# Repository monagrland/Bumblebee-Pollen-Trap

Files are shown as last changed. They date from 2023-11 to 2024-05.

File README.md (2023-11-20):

# Pollenstripper
 
This repository contains .scad and STL files as well as json presets for the bumblebee pollenstripper as described in Krüger et al

## Printing the Files

If you just want to print the files used in Krüger et al, you can go to the "STL_Files" directory and download all STL files that you want to print. Almost all files can be easily printed in PLA or PETG. If you want to use the pollen for DNA sequencing, we would recommend to use thermostable materials like ASA or ABS, to be able to clean the parts with boiling water. Almost all files can be printed without supports, with the exception of the funnel. The corpus minorly profits from supports but they are not a necessity.

# DIY Pollenstripper
## Getting Started
Do you have ideas to improve the Pollenstripper? Feel free to modify the design however you want. A lot of modifications can be done without any knowledge in 3D-Design. All you need are the files in this repository and the open source software [OpenSCAD](https://openscad.org/). It can be freely downloaded from the website. 

After installing OpenSCAD you can download this repository by clicking on "Code" and selecting "Download ZIP". After finishing the download you can unpack the directory to you prefered path.
Now you can chose which parts you want to modify. 

If you want to modify the corpus, the darkener or the funnel, you can open the corpus_designer.scad file with OpenSCAD. If you want to modify the filter inserts, you can open the filter_designer.scad file with OpenSCAD.
After opening the file you should see by default four different windows. On the Left the **Editor** shows you the code used to create the designs. On the bottom you can see the **Console**, which offers information about the rendering and if there were occuring errors. In the middle you can see the current preview of your 3D-Object. On the fourth panel on the right you can find the **Customizer**. If the Customizer is not open, you can open it by clicking on the **Window** menu and unselecting the **Hide customizer** option.
You can update the preview by pressing F5 and you can render the model with F6.

For further information about OpenSCAD, take a look at the [docs](https://openscad.org/documentation.html).  

## DIY Corpus, Darkener, Funnel & Brush-Corpus
If you want to modify the corpus, the darkener, the funnel or the brush-corpus you have two different options: either you use the customizer and play around with the options available without the need of any knowledge regarding 3D-design or programming or you can modify the code itself to create something completely custom. 
If you want to use the customizer, the variables are seperated into different tabs.

### Presets
If you don't want to create your designs from scratch, you can also use one of the available presets. You can find the presets at the top of the customizer. The preset *corpus* contains the settings for the corpus used in Krüger et al, while the preset *corpus with grid* has the same settings but with a grid at the bottom of the corpus. The *darkener* preset contains the settings for the darkener used in Krüger et al.

### Parameters
In the `Parameters` tab you can select which part you want to create or modify. 

### Acrylic Cube
In the `Acrylic Cube` tab you can select the dimensions of the acrylic cube that you are going to use. This is important for all designs since they are automaticallly modified to fit differently sized acrylic cubes.

### Darkener
The `Darkener` tab contains variables that are only relevant if you want to modify the darkener.

### Insert
In the `Insert` tab you have to enter the dimensions of the filter inserts that are created with the filter_designer.scad file. This is important for the corpus and brush-corpus designs so that the filter inserts fit into the slots.
You can also modify the positioning of the slot and the space between the filter insert and the corpus. 

### Corpus Basics
The `Corpus Basics` tab containts the variables that are used to create the corpus design. The first part of the corpus depends on the size of the acrylic cube and has to be modified in the corresponding tab. The second part of the corpus is made out of "tubes", which are basically small chambers which each contain a single slot for a filter insert. You can modify the dimensions of these tubes and the amount of tubes that are put behind each other to modify the amount of "chambers" the bumblebee has to cross.

### Grid Pattern
In earlier iterations, the corpus had a grid at the bottom where the pollen was supposed to fall through. In our testing this did not work as expected, which is why the grid was removed to decrease the amount of light that falls into the chambers to focus the bumblebees more into the direction of the exit. If you want you can create the grid in this tab and modify the dimensions and the amount of the squared holes in the corpus.

### Brush
We tested a version of the pollenstripper where brushes were mounted at an angle allowing the bumblebee to press itself through the middle between the brushes. This version did not succeed in any case, but if you want to modify it you can change the parameters at the `Brush` tab.

### Funnel
Earlier iterations had a grid where the pollen was supposed to fall through (see grid tab). Aterwards the pollen was supposed to fall into a funnel which could be slid onto the corpus with a thread for 2ml microcentrifuge tubes at the bottom. If you want to create or modify this funnel, you can find the needed variables at the `Funnel` tab.

### Misc
The `Misc` tab only contains the $fn variable which is used to define the number of fragments used to draw an arc. A higher value creates smoother arcs but also significantly increases the rendering time. If you just want to play around with the values i would recommend a lower $fn, for example 25, and to later increase it after you finished your model and create the rendering for the export of the file. My recommendation herefore would be a value of 100.

## DIY Filter Inserts
If you want to create or modify the filter inserts, you can either use the customizer and play around with the options available without the need of any knowledge regarding 3D-Design or programming or you can modify the code itself to create something completely custom
If you want to use the customizer, the variables here are also seperated into different tabs.

### Presets
If you don't want to create your designs from scratch, you can also use one of the available presets. You can find the presets at the top of the customizer. The preset *Preset a* contains the settings for the filter insert *a* as described in Krüger et al, while *Preset b* and *Preset c* are used for the other two described filter inserts. To recreate all filter inserts from the publication you can select the presets and just edit the diameter of the hole inside the `Base Plate` tab. 

### Base Plate
The `Base Plate` tab allows changes to the dimensions of the base plate, the bars on the base plate as well as the text on top of the base plate.

### Hole Structure
In the `Hole Structure` tab you select which one of the five possible designs you want to use.
You can choose if you want no structure ("None"), slides (used in version *a* in Krüger et al.), two different triangle structures ("triangle" and "triangle2", used in version *b* and *c*, respectively) (used in version c) or concentric (untested idea using concentric circles). 

### Hole Structure == Slides
If you chose the "slides" hole structure in the `Hole Structure` tab, you can edit the remainding variables in the `Hole Structure == Slides` tab. Here you can change the dimensions of the rings as well as the dimensions, offset and number of slides.

### Hole Structure == Triangle
If you chose the "triangle" hole structure in the `Hole Structure` tab, you can edit the remainding variables in the `Hole Structure == Triangle` tab. Here you can change the dimensions of the rings as well as the dimensions and number of triangles.

### Hole Structure == Triangle2
If you chose the "triangle2" hole structure in the `Hole Structure` tab, you can edit the remainding variables in the `Hole Structure == Triangle2` tab. Here you can change the dimensions of the rings as well as the dimensions and number of triangles.

### Hole Structure == Concentric
If you chose the "concentric" hole structure in the `Hole Structure` tab, you can edit the remainding variables in the `Hole Structure == Concentric` tab. Here you can change the dimensions and positioning of the concentric rings.

### Misc
The `Misc` tab only contains the $fn variable which is used to define the number of fragments used to draw an arc. A higher value creates smoother arcs but also significantly increases the rendering time. If you just want to play around with the values I would recommend a lower $fn, for example 25, and to later increase it after you finished your model and create the rendering for the export of the file. My recommendation therefore would be a value of 100.

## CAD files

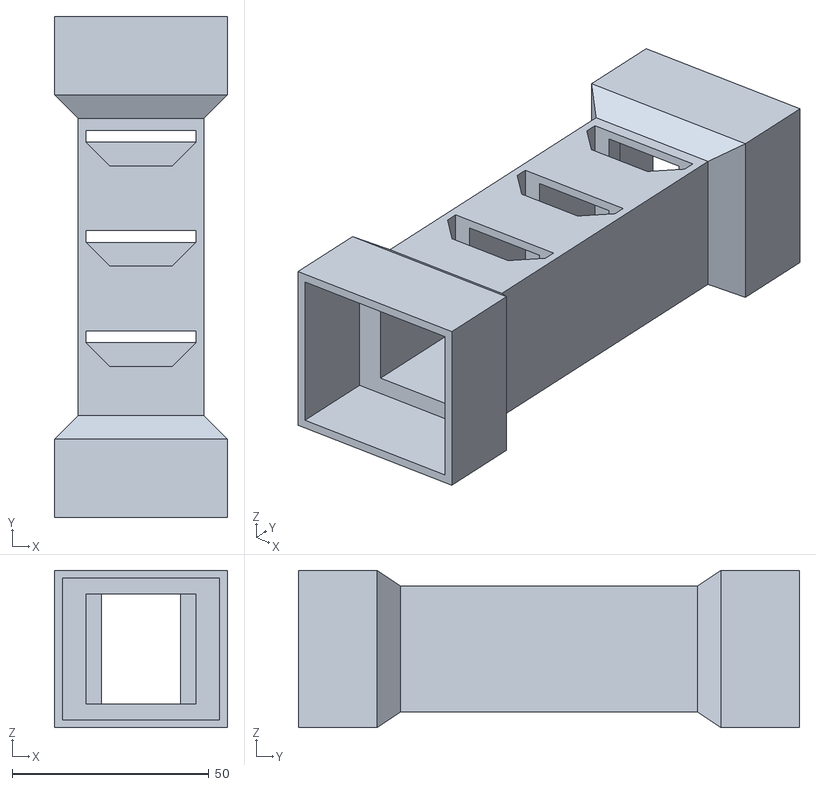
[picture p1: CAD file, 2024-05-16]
STL_Files/Corpus_Double_Cube.stl
44.0 x 127.5 x 40.0

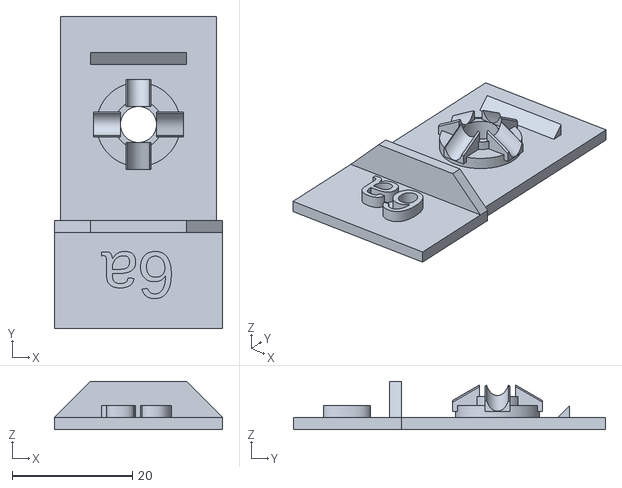
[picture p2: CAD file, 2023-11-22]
STL_Files/a_6_0.stl
28.0 x 52.0 x 8.00

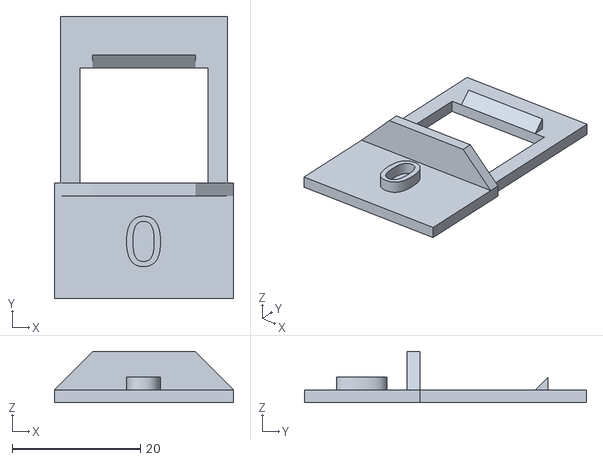
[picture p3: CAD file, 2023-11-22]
STL_Files/Filter_Brush.stl
28.0 x 44.0 x 8.00

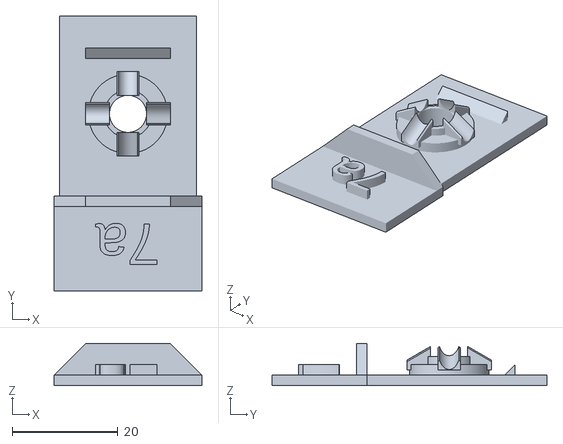
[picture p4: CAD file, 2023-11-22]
STL_Files/a_7_0.stl
28.0 x 52.0 x 8.00

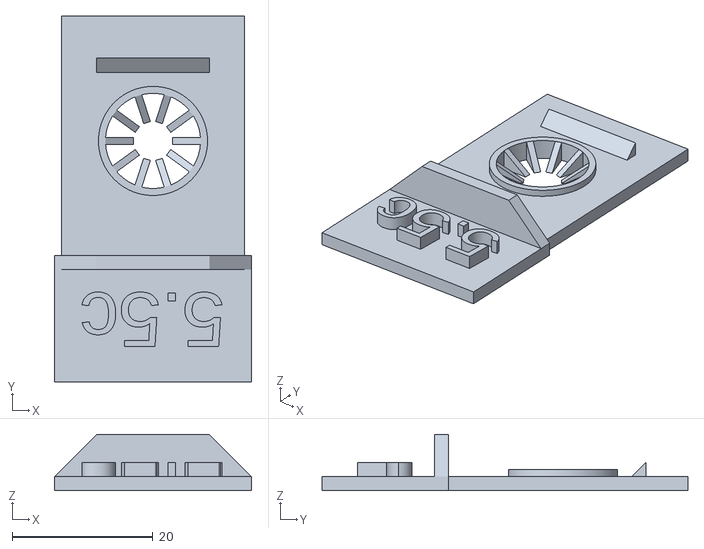
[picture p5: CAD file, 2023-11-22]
STL_Files/c_5_5.stl
28.0 x 52.0 x 8.00

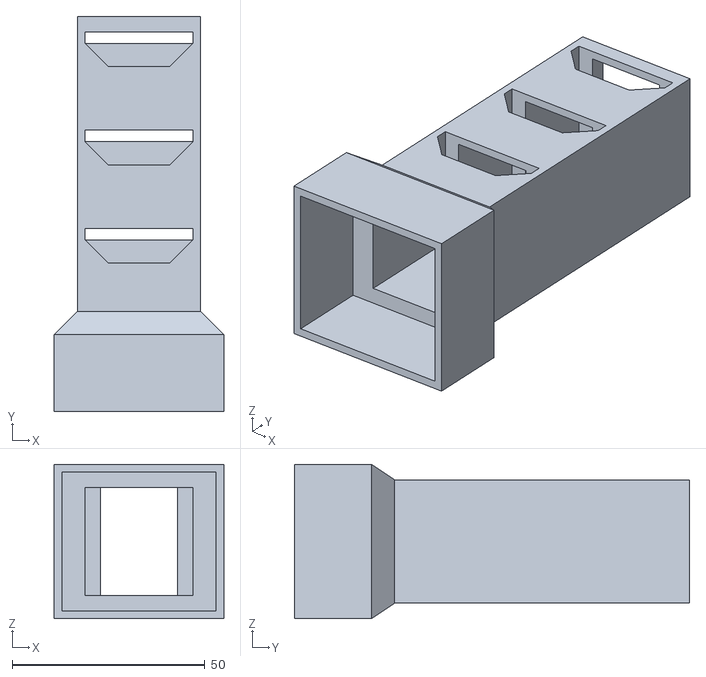
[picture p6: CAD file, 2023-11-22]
STL_Files/Corpus_sans_holes.stl
44.0 x 102.5 x 40.0

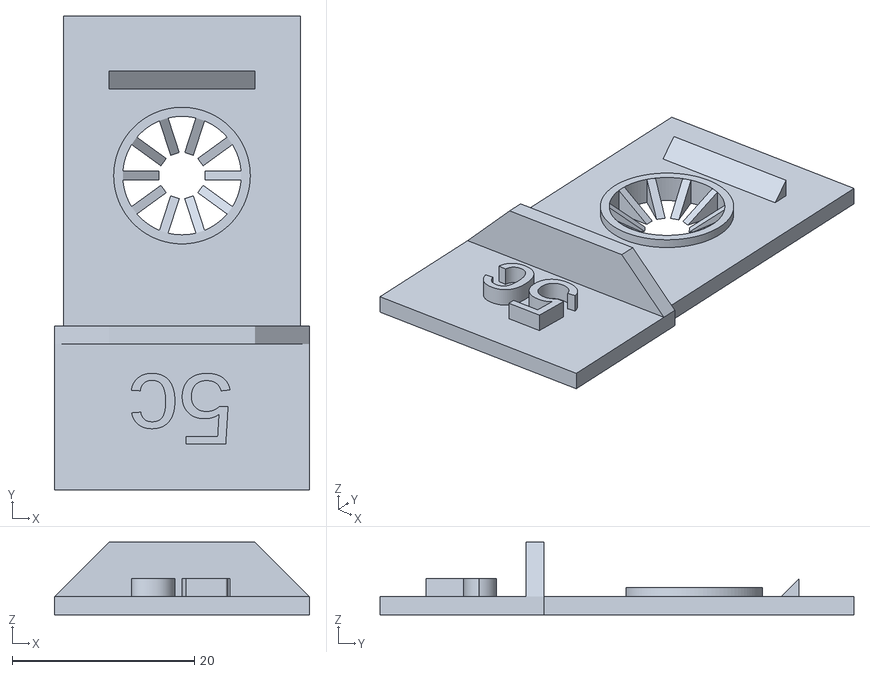
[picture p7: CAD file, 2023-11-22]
STL_Files/c_5_0.stl
28.0 x 52.0 x 8.00

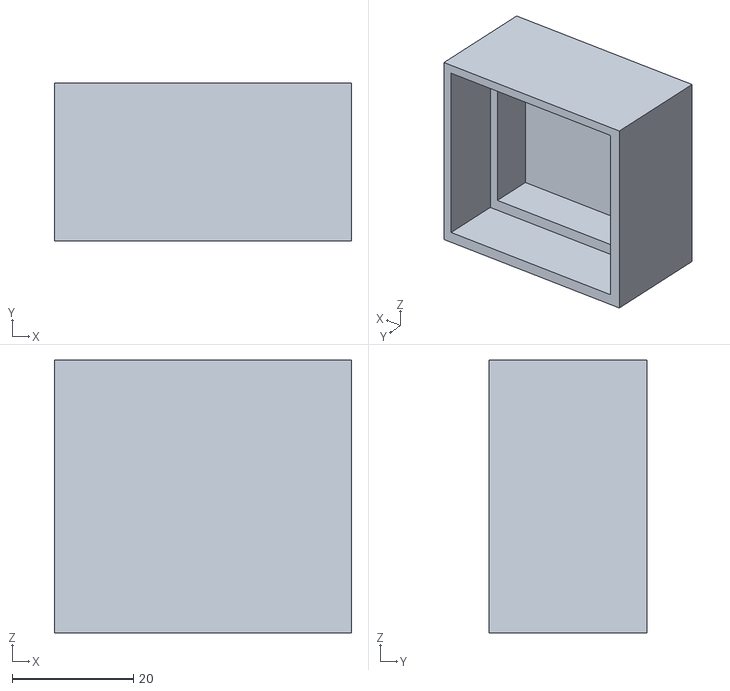
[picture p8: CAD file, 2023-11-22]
STL_Files/Darkener.stl
49.0 x 26.0 x 45.0

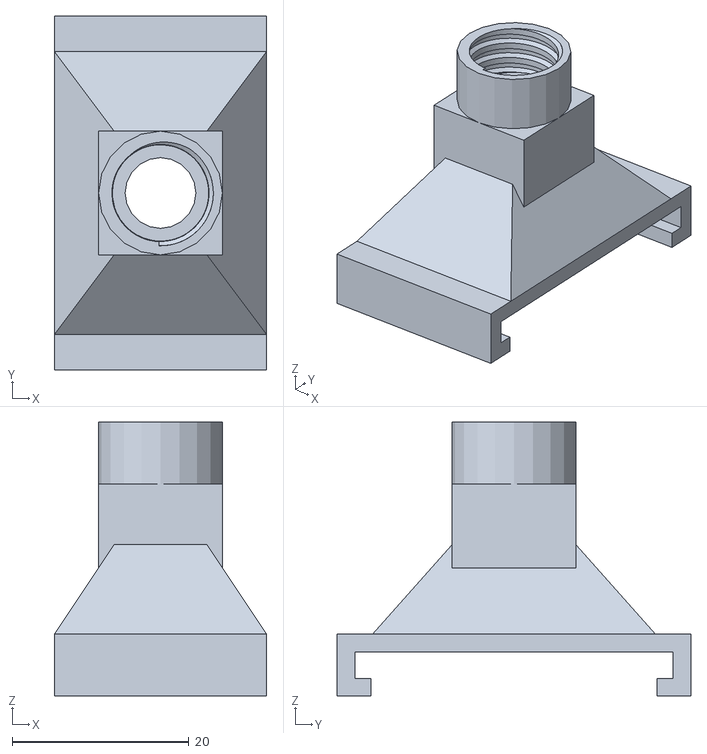
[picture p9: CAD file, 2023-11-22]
STL_Files/Funnel_Brush.stl
24.0 x 40.0 x 31.0

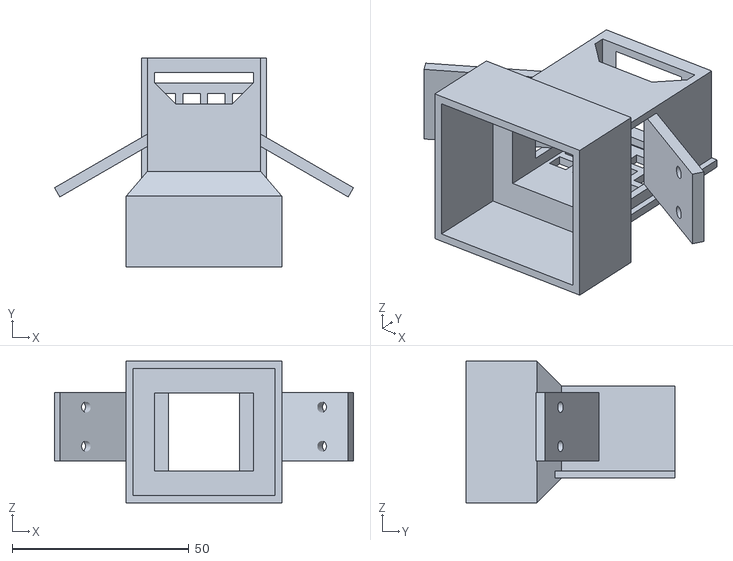
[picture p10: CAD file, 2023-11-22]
STL_Files/Corpus_Brush.stl
84.5 x 59.0 x 40.0

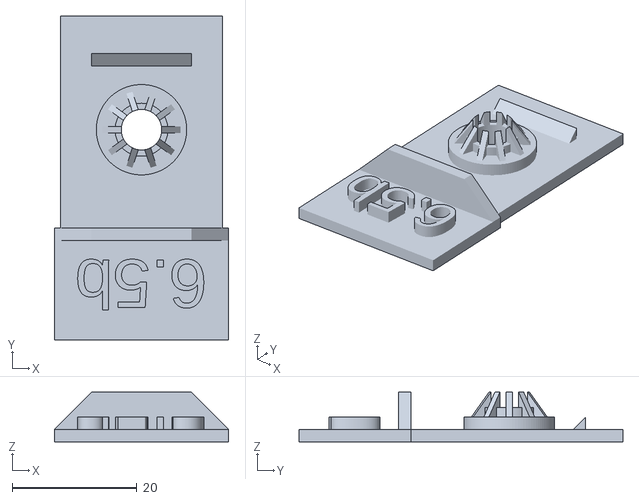
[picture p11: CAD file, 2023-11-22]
STL_Files/b_6_5.stl
28.0 x 52.0 x 8.00

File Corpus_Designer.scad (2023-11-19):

 //Variables
// Select which part you want to create: corpus is the main part of the pollenstripper, corpus_brush is a version of the pollenstripper with angled mounts for brushes, the darkener is a part that sits on top of the plexiglas cube to keep light from getting in and the funnel was meant to collect the pollen after it fell off and through the grid (deprecated)
cube_design = "corpus"; // [corpus, corpus_brush, darkener, funnel]

/* [Acrylic Cube] */
plexi_cube_width = 39; //39 for cube1, 32 for cube2
plexi_cube_length = 35; //35 for cube1, 30 for cube2
plexi_cube_depth_overall = 30;
plexi_cube_depth = 20; //this is for the main corpus
plexi_cube_thickness = 2;
plexi_cube_buffer = 0.5; //1mm room in every direction

/* [Darkener] */
// The length that the darkener overlaps with the corpus
darkener_overhang = 10;

/* [Insert] */
//needs to be the same as in the insert creator
insert_bar_height = 6;
//needs to be the same as in the insert creator
insert_bar_length = 16;
//needs to be the same as "base plate length upper" in the insert creator
insert_base_length = 28;
//needs to be the same as "base plate thickness" in the insert creator
insert_thickness = 2;
// buffer space between corpus and insert
insert_buffer = 1;
// distance of the insert from the end of the tube. CAREFUL: changing this can break the design, default=4
insert_distance_from_tube_end = 4;

/* [Corpus Basics] */
//thickness of the tubes (lower parts of the corpus containing the inserts)
tube_thickness = 2;
//width of the tubes
tube_width = 28;
//length of the tubes
tube_length = 28;
//depth of the tubes, 25.5 for normal corpus design, 32 for brush
tube_depth = 25.5; // was 38.5, for normal design 25.5, increase for brush to 32
//number of tubes
tube_count = 3;

// width of the bar that locks the inserts so that they can't move to the back, CAREFUL: changing this will break the design, default = 4
security_bar_width = 4;
slide_bar_length = tube_depth+2;
// width of the bar the funnel slides on
slide_bar_width = 1.6; //decreased from 2 to 1,6 for buffer
//height of the bar the funnel slides on
slide_bar_height = 2;

/* [Grid Pattern] */
// grid pattern, meant to let the stripped pollen fall through into the funnel
grid_pattern = "None"; //[None, squares, squares2]
//width of the squares
square_width = 5;
//length of the squares
square_length = 4;
//distance between the squares
square_distance = 2;
//number oif squares per row
number_squares_per_row = 4;
//number of squares per column, suggestion for normal corpus 2, for brush 3
number_squares_per_column = 3;

/* [Brush] */
// length of the top part of the brush
brush_head_length = 16;
// length of the bottom part of the brush
brush_bottom_length = 24;
// width of the brush
brush_width = 19.25;
// thickness of the brush
brush_thickness = 5.5;
// distance of the screw holes from the top of the brush
distance_hole_from_top = 1.6;
// distance of the screw holes from the side of the brush
distance_hole_from_side = 2.6;
// diameter of the screw holes
diameter = 3;

/* [Funnel] */
// width of the bars that slide on the corpus
funnel_slide_width = 4;
// height of the bars that slide on the corpus
funnel_slide_height = 7;
// height of the hollow part of the bars that slide on the corpus
funnel_slide_hollow_height = 3;
// buffer between the corpus bar and the funnel slide bar
funnel_slide_buffer_width = 0.2;
// length of the pyramid
funnel_pyramid_length = 32;
// height of the tip of the pyramid part
funnel_pyramid_tip_height = 18;
// width of the cube at the top of the funnel
funnel_tip_cube_width = 14;
// length of the cube at the top of the funnel
funnel_tip_cube_length = 14;
// height of the cube at the top of the funnel
funnel_tip_cube_height = 11;
// height of the cylinder that hollows out the top of the funnel
funnel_hollow_cylinder_height = 20;
// diameter of the cylinder that hollows out the top of the funnel
funnel_hollow_cylinder_diameter = 7;



/* [Misc] */
// Number of Faces: higher number is good for smoother curved areas, lower number significantly decreases rendering time, recommending 25 for playing around and 100 for exporting
$fn = 50;

//angle
tube_distance_left = (plexi_cube_width/2+plexi_cube_buffer+plexi_cube_thickness-tube_width/2-tube_thickness);
tube_distance_bottom = (plexi_cube_length/2+plexi_cube_buffer+plexi_cube_thickness-tube_length/2-tube_thickness);
angle_depth = max(tube_distance_left, tube_distance_bottom);
outer_cube_width = plexi_cube_width + 2*plexi_cube_thickness + 2*plexi_cube_buffer;
outer_cube_length = plexi_cube_length + 2*plexi_cube_thickness + 2*plexi_cube_buffer;

//module to create triangles
module triangle(width,length,height){
    difference(){
        cube([width,length,height]);
        rotate([0,0,45]) cube([width*2.5,length*2.5,height*5]);
    }
}

//module to show points of a polyhedron
module showPoints(v) {
    for (i = [0: len(v)-1]) {
        translate(v[i]) color("red") 
        text(str(i), font = "Courier New", size=1.5);
         
    }
}

//module to create a square grid pattern
module square_grid(){
    grid_width = square_width*number_squares_per_row + square_distance*(number_squares_per_row-1);
    grid_length = square_length*number_squares_per_column + square_distance*(number_squares_per_column-1);
translate([tube_width/2+tube_thickness-grid_width/2,tube_depth+angle_depth-(insert_distance_from_tube_end+insert_thickness+insert_buffer+insert_bar_height)+3,0])
translate([grid_width,0,0])
rotate([0,0,180])
for (j=[0:number_squares_per_column-1]){
for (i=[0:number_squares_per_row-1]){
    translate([i*(square_distance+square_width),j*(square_distance+square_length),0])cube([square_width,square_length,tube_thickness]);
    }
}
}

module square_grid2(){
    grid_width = square_width*number_squares_per_row + square_distance*(number_squares_per_row-1);
    grid_length = square_length*number_squares_per_column + square_distance*(number_squares_per_column-1);
translate([tube_width/2+tube_thickness-grid_width/2,tube_depth+angle_depth-(insert_distance_from_tube_end+insert_thickness+insert_buffer+insert_bar_height),0])
translate([grid_width-square_length/2,0,0])
rotate([0,0,180])
for (j=[0:number_squares_per_column-1]){
for (i=[0:number_squares_per_row-1]){
    translate([i*(square_distance+square_width),j*(square_distance+square_length),0])rotate([0,0,45])cube([square_width,square_length,tube_thickness]);
    }
}
}

//module to create a brush as a standin
module brush (){
difference(){
union(){
color("green")cube([brush_width, brush_thickness, brush_head_length]);
color("brown")translate([0,0,brush_head_length])cube([brush_width, brush_thickness, brush_bottom_length]);
}

union(){
translate([diameter/2+distance_hole_from_side,0,diameter/2 + distance_hole_from_top])rotate([270,0,0])cylinder(h=brush_thickness, d=diameter);
translate([brush_width-diameter/2-distance_hole_from_side,0,diameter/2 + distance_hole_from_top])rotate([270,0,0])cylinder(h=brush_thickness, d=diameter);
}
}
}

//module to create a mount for the brush
module brush_mount (){
difference(){
union(){
color("green")cube([brush_width, brush_thickness, brush_head_length]);
color("brown")translate([0,0,brush_head_length])cube([brush_width, brush_thickness, brush_bottom_length]);
}

union(){
translate([diameter/2+distance_hole_from_side,0,diameter/2 + distance_hole_from_top])rotate([270,0,0])cylinder(h=brush_thickness, d=diameter);
translate([brush_width-diameter/2-distance_hole_from_side,0,diameter/2 + distance_hole_from_top])rotate([270,0,0])cylinder(h=brush_thickness, d=diameter);
}
}
}


if (cube_design == "corpus"){
union(){

//plexi_cube part of the tube
difference(){
    cube([plexi_cube_width + 2*plexi_cube_thickness + 2*plexi_cube_buffer, plexi_cube_depth, plexi_cube_length+2*plexi_cube_thickness + 2*plexi_cube_buffer]);
    translate([plexi_cube_thickness,0,plexi_cube_thickness])cube([plexi_cube_width + 2*plexi_cube_buffer, plexi_cube_depth, plexi_cube_length + 2*plexi_cube_buffer]);
}

//angle
angle_points = [
    [0,0,0], //0
    [outer_cube_width,0,0],//1
    [outer_cube_width,0,outer_cube_length],//2
    [0,0,outer_cube_length],//3
    [tube_distance_left,0,tube_distance_bottom],//4
    [outer_cube_width-tube_distance_left,0,tube_distance_bottom],//5
    [outer_cube_width-tube_distance_left,0,outer_cube_length-tube_distance_bottom],//6
    [tube_distance_left,0,outer_cube_length-tube_distance_bottom],//7
    [tube_distance_left,angle_depth,tube_distance_bottom],//8
    [outer_cube_width-tube_distance_left,angle_depth,tube_distance_bottom],//9
    [outer_cube_width-tube_distance_left,angle_depth,outer_cube_length-tube_distance_bottom],//10
    [tube_distance_left,angle_depth,outer_cube_length-tube_distance_bottom],//11
    
];

*showPoints(angle_points);
angle_faces = [
    [1,0,4,5],
    [0,1,9,8],
    [5,4,8,9],
    [2,1,5,6],
    [1,2,10,9],
    [6,5,9,10],
    [3,2,6,7],
    [2,3,11,10],
    [7,6,10,11],
    [0,3,7,4],
    [3,0,8,11],
    [4,7,11,8],
];
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

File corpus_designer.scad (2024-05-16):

 //Variables
// Select which part you want to create: corpus is the main part of the pollenstripper, corpus_brush is a version of the pollenstripper with angled mounts for brushes, the darkener is a part that sits on top of the plexiglas cube to keep light from getting in and the funnel was meant to collect the pollen after it fell off and through the grid (deprecated)
cube_design = "corpus"; // [corpus, corpus_dual_cube, corpus_brush, darkener, funnel]

/* [Acrylic Cube] */
plexi_cube_width = 39; //39 for cube1, 32 for cube2
plexi_cube_length = 35; //35 for cube1, 30 for cube2
plexi_cube_depth_overall = 30;
plexi_cube_depth = 20; //this is for the main corpus
plexi_cube_thickness = 2;
plexi_cube_buffer = 0.5; //1mm room in every direction

/* [Acrylic Cube 2: Only necessary for dual cube corpus] */
plexi_cube_width2 = 39; //39 for cube1, 32 for cube2
plexi_cube_length2 = 35; //35 for cube1, 30 for cube2
plexi_cube_depth_overall2 = 30;
plexi_cube_depth2 = 20; //this is for the main corpus
plexi_cube_thickness2 = 2;
plexi_cube_buffer2 = 0.5; //1mm room in every direction

/* [Darkener] */
// The length that the darkener overlaps with the corpus
darkener_overhang = 10;

/* [Insert] */
//needs to be the same as in the insert creator
insert_bar_height = 6;
//needs to be the same as in the insert creator
insert_bar_length = 16;
//needs to be the same as "base plate length upper" in the insert creator
insert_base_length = 28;
//needs to be the same as "base plate thickness" in the insert creator
insert_thickness = 2;
// buffer space between corpus and insert
insert_buffer = 1;
// distance of the insert from the end of the tube. CAREFUL: changing this can break the design, default=4
insert_distance_from_tube_end = 4;

/* [Corpus Basics] */
//thickness of the tubes (lower parts of the corpus containing the inserts)
tube_thickness = 2;
//width of the tubes
tube_width = 28;
//length of the tubes
tube_length = 28;
//depth of the tubes, 25.5 for normal corpus design, 32 for brush
tube_depth = 25.5; // was 38.5, for normal design 25.5, increase for brush to 32
//number of tubes
tube_count = 3;

// width of the bar that locks the inserts so that they can't move to the back, CAREFUL: changing this will break the design, default = 4
security_bar_width = 4;
slide_bar_length = tube_depth+2;
// width of the bar the funnel slides on
slide_bar_width = 1.6; //decreased from 2 to 1,6 for buffer
//height of the bar the funnel slides on
slide_bar_height = 2;

/* [Grid Pattern] */
// grid pattern, meant to let the stripped pollen fall through into the funnel
grid_pattern = "None"; //[None, squares, squares2]
//width of the squares
square_width = 5;
//length of the squares
square_length = 4;
//distance between the squares
square_distance = 2;
//number oif squares per row
number_squares_per_row = 4;
//number of squares per column, suggestion for normal corpus 2, for brush 3
number_squares_per_column = 3;

/* [Brush] */
// length of the top part of the brush
brush_head_length = 16;
// length of the bottom part of the brush
brush_bottom_length = 24;
// width of the brush
brush_width = 19.25;
// thickness of the brush
brush_thickness = 5.5;
// distance of the screw holes from the top of the brush
distance_hole_from_top = 1.6;
// distance of the screw holes from the side of the brush
distance_hole_from_side = 2.6;
// diameter of the screw holes
diameter = 3;

/* [Funnel] */
// width of the bars that slide on the corpus
funnel_slide_width = 4;
// height of the bars that slide on the corpus
funnel_slide_height = 7;
// height of the hollow part of the bars that slide on the corpus
funnel_slide_hollow_height = 3;
// buffer between the corpus bar and the funnel slide bar
funnel_slide_buffer_width = 0.2;
// length of the pyramid
funnel_pyramid_length = 32;
// height of the tip of the pyramid part
funnel_pyramid_tip_height = 18;
// width of the cube at the top of the funnel
funnel_tip_cube_width = 14;
// length of the cube at the top of the funnel
funnel_tip_cube_length = 14;
// height of the cube at the top of the funnel
funnel_tip_cube_height = 11;
// height of the cylinder that hollows out the top of the funnel
funnel_hollow_cylinder_height = 20;
// diameter of the cylinder that hollows out the top of the funnel
funnel_hollow_cylinder_diameter = 7;



/* [Misc] */
// Number of Faces: higher number is good for smoother curved areas, lower number significantly decreases rendering time, recommending 25 for playing around and 100 for exporting
$fn = 50;

//angle
tube_distance_left = (plexi_cube_width/2+plexi_cube_buffer+plexi_cube_thickness-tube_width/2-tube_thickness);
tube_distance_bottom = (plexi_cube_length/2+plexi_cube_buffer+plexi_cube_thickness-tube_length/2-tube_thickness);
angle_depth = max(tube_distance_left, tube_distance_bottom);
outer_cube_width = plexi_cube_width + 2*plexi_cube_thickness + 2*plexi_cube_buffer;
outer_cube_length = plexi_cube_length + 2*plexi_cube_thickness + 2*plexi_cube_buffer;

//angle2
tube_distance_left2 = (plexi_cube_width2/2+plexi_cube_buffer2+plexi_cube_thickness2-tube_width/2-tube_thickness);
tube_distance_bottom2 = (plexi_cube_length2/2+plexi_cube_buffer2+plexi_cube_thickness2-tube_length/2-tube_thickness);
angle_depth2 = max(tube_distance_left2, tube_distance_bottom2);
outer_cube_width2 = plexi_cube_width2 + 2*plexi_cube_thickness2 + 2*plexi_cube_buffer2;
outer_cube_length2 = plexi_cube_length2 + 2*plexi_cube_thickness2 + 2*plexi_cube_buffer2;

//module to create triangles
module triangle(width,length,height){
    difference(){
        cube([width,length,height]);
        rotate([0,0,45]) cube([width*2.5,length*2.5,height*5]);
    }
}

//module to show points of a polyhedron
module showPoints(v) {
    for (i = [0: len(v)-1]) {
        translate(v[i]) color("red") 
        text(str(i), font = "Courier New", size=1.5);
         
    }
}

//module to create a square grid pattern
module square_grid(){
    grid_width = square_width*number_squares_per_row + square_distance*(number_squares_per_row-1);
    grid_length = square_length*number_squares_per_column + square_distance*(number_squares_per_column-1);
translate([tube_width/2+tube_thickness-grid_width/2,tube_depth+angle_depth-(insert_distance_from_tube_end+insert_thickness+insert_buffer+insert_bar_height)+3,0])
translate([grid_width,0,0])
rotate([0,0,180])
for (j=[0:number_squares_per_column-1]){
for (i=[0:number_squares_per_row-1]){
    translate([i*(square_distance+square_width),j*(square_distance+square_length),0])cube([square_width,square_length,tube_thickness]);
    }
}
}

module square_grid2(){
    grid_width = square_width*number_squares_per_row + square_distance*(number_squares_per_row-1);
    grid_length = square_length*number_squares_per_column + square_distance*(number_squares_per_column-1);
translate([tube_width/2+tube_thickness-grid_width/2,tube_depth+angle_depth-(insert_distance_from_tube_end+insert_thickness+insert_buffer+insert_bar_height),0])
translate([grid_width-square_length/2,0,0])
rotate([0,0,180])
for (j=[0:number_squares_per_column-1]){
for (i=[0:number_squares_per_row-1]){
    translate([i*(square_distance+square_width),j*(square_distance+square_length),0])rotate([0,0,45])cube([square_width,square_length,tube_thickness]);
    }
}
}

//module to create a brush as a standin
module brush (){
difference(){
union(){
color("green")cube([brush_width, brush_thickness, brush_head_length]);
color("brown")translate([0,0,brush_head_length])cube([brush_width, brush_thickness, brush_bottom_length]);
}

union(){
translate([diameter/2+distance_hole_from_side,0,diameter/2 + distance_hole_from_top])rotate([270,0,0])cylinder(h=brush_thickness, d=diameter);
translate([brush_width-diameter/2-distance_hole_from_side,0,diameter/2 + distance_hole_from_top])rotate([270,0,0])cylinder(h=brush_thickness, d=diameter);
}
}
}

//module to create a mount for the brush
module brush_mount (){
difference(){
union(){
color("green")cube([brush_width, brush_thickness, brush_head_length]);
color("brown")translate([0,0,brush_head_length])cube([brush_width, brush_thickness, brush_bottom_length]);
}

union(){
translate([diameter/2+distance_hole_from_side,0,diameter/2 + distance_hole_from_top])rotate([270,0,0])cylinder(h=brush_thickness, d=diameter);
translate([brush_width-diameter/2-distance_hole_from_side,0,diameter/2 + distance_hole_from_top])rotate([270,0,0])cylinder(h=brush_thickness, d=diameter);
}
}
}


if (cube_design == "corpus"){
union(){

//plexi_cube part of the tube
difference(){
    cube([plexi_cube_width + 2*plexi_cube_thickness + 2*plexi_cube_buffer, plexi_cube_depth, plexi_cube_length+2*plexi_cube_thickness + 2*plexi_cube_buffer]);
    translate([plexi_cube_thickness,0,plexi_cube_thickness])cube([plexi_cube_width + 2*plexi_cube_buffer, plexi_cube_depth, plexi_cube_length + 2*plexi_cube_buffer]);
}
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

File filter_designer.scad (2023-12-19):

//Variables
/* [Base Plate] */
//length of the lower part of the base plate
base_plate_length_lower = 26;
//length of the upper part of the base plate
base_plate_length_upper = 28;
//width of the lower part of the base plate
base_plate_width_lower = 34;
//length of the upper part of the base plate
base_plate_width_upper = 18;
//thickness of the baseplate
base_plate_thickness = 2;
// type of bar, newer versions only use "angled"
bar_type = "angled"; // [angled, bar]
// length of the bar
bar_length = 16;
// width of the bar
bar_width = 2;
// height of the bar
bar_height = 6;

//diameter of the hole, also input for the text at the top
diameter_hole = 5.5;
// thickness of the text at the top
diameter_text_thickness = 2;
// size of the text at the top
diameter_text_size = 8;

// additional text at the top
identifier = "a";

// width of the lower bar
lower_bar_width = 2;
// height of the lower bar
lower_bar_height = 2;
// distance from the bottom of the base plate to the lower bar
lower_bar_distance_from_bottom = 6;

/* [Hole Structure] */
// structure of the design around the hole
hole_structure = "triangle2"; //  [None, slides, triangle, triangle2, concentric, brush]

/* [Hole Structure == Slides] */
// width of the outer ring
outer_ring_width_slides = 4.0;
// height of the outer ring
outer_ring_height_slides = 2.0;
// width of the inner ring
inner_ring_width_slides = 1.0;
// height of the outer ring
inner_ring_height_slides = 1.5;
// number of slides, will be automatically oriented around the center of the hole
number_slides = 4;

// multiplier for the width of the slides
slide_width_factor = 0.7;
// multiplier for the length of the slides
slide_length_factor = 1;
// multiplier for the height of the slides
slide_height_factor = 1;
// offset of the slides from the center of the hole
slide_offset_from_center = 0;

/* [Hole Structure == Triangle] */
// width of the outer ring
outer_ring_width_triangle = 4.0;
// height of the outer ring
outer_ring_height_triangle = 2.0;
// width of the inner ring
inner_ring_width_triangle = 1.0;
// height of the inner ring
inner_ring_height_triangle = 1.5;
// number of bars, will be automatically oriented around the center of the hole
number_bars_triangle = 10;
// height of the triangles
triangle_height = 4;
// length of the triangles
triangle_length = 3;
// thickness of the triangles
triangle_thickness = 1;

/* [Hole Structure == Triangle2] */
// width of the outer ring
outer_ring_width_triangle2 = 4.0;
// height of the outer ring
outer_ring_height_triangle2 = 2.0;
// width of the inner ring
inner_ring_width_triangle2 = 1.0;
// height of the inner ring
inner_ring_height_triangle2 = 1.5;
// number of bars, will be automatically oriented around the center of the hole
number_bars_triangle2 = 10;
// height of the triangles
triangle2_height = 4;
// length of the triangles
triangle2_length = 3;
// thickness of the triangles
triangle2_thickness = 1;

/* [Hole Structure == Concentric] */
// height of the cone, careful, cant be higher than the upper bar or it will get stuck!
concentric_height = 6;
// starting point of the concentric rings, 
concentric_ring_height = 1.5;
// distance top to bottom hole
concentric_distance_top_bottom_hole = 6;
// width of the concentric rings
concentric_ring_width = 1;

/* [Misc] */
// Number of Faces: higher number is good for smoother curved areas, lower number significantly decreases rendering time, recommending 25 for playing around and 100 for exporting
$fn = 25;


//module to show points of a polyhedron, see https://gusmith.wordpress.com/tag/openscad/
module showPoints(v) {
    for (i = [0: len(v)-1]) {
        translate(v[i]) color("red")
        text(str(i), font = "Courier New", size=1.5);

    }
}

//module to create slides for the filter
module slide (){
    width = 5.5;
    length = 4.5;
    height = 5;
    angle = 30;
difference(){
    render()intersection(){
    union(){
    translate([0,3.1,0.5])
    difference(){
    difference(){
    translate([0,0,height/2])
    rotate([angle,0,0])
    difference(){
    scale([width*1.64,length*2.1,height*1.18]) sphere(d=1);
    translate([0,0,2])rotate([90,0,180])cylinder(h=40,d1=6,d2=6,center=true);
    }
    translate([-(length),6-(width*1.65)/2,0])cube([width*2,length*1.5,height*2]);
}
    union(){
    translate([width*1.05,-length/2,height])cube([width,length*2,height*2],center=true);
    translate([-width*1.05,-length/2,height])cube([width,length*2,height*2],center=true);
    }
    translate([-width,-length*2.7,-height])cube([width*2,length*2,height*2]);
}
    infill_length = 6.05/2;
    infill_width = 1.4;
    infill_height = 4.5;
    infill_points=[
    [1.27,0,0], //0 base
    [infill_length,0,0], //1
    [infill_length,0,infill_height], //2
    [0,0,infill_height], //3
    [infill_length,infill_width,0], //4
    [infill_length,infill_width,infill_height], //5
    [0,infill_width,infill_height], //6
    [0,infill_width,infill_height*1.5/2], //7
    [0,0,infill_height/2] //8
    ];

    infill_faces = [
    [8,3,2,1,0],
    [0,1,4],
    [1,2,5,4],
    [3,6,5,2],
    [3,8,7,6],
    [8,0,7],
    [7,0,4],
    [4,5,6,7]
    ];
    *showPoints(infill_points);
    translate([0,0,0])rotate([90,0,180])polyhedron(infill_points, infill_faces);

    mirror([1,0,0])rotate([90,0,180])polyhedron(infill_points, infill_faces);
}
    translate([(-width*1.1)/2,0,0])cube([width*1.1,length,height*2]);
}
translate([0,0,-0.6])translate([1.5,length/2-3,height/2+0.2])rotate([30,0,0])rotate([0,30,0])cube([2,length*1.5,2]);
translate([0,0,-0.6])translate([-3.5,-((length/2-3)+1),(height/2+0.2)-1])rotate([30,0,0])rotate([0,330,0])cube([2,length*1.5,2]);

}
}
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

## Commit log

2022-06-11 Release candidate
    [Filter_Designer.scad]
2022-06-12 Changed the bar to an angled version
    The code for the angled bar is mostly copied from the corpus creator, needs cleanup.
    [Filter_Designer.scad]
2022-06-12 Added Square Pattern, slde and insert slot
2022-06-30 added file extension to Corpus_designer
    [Corpus_Designer.scad]
2022-06-30 Create Corpus_Designer_v2
    Created a second Corpus Design with the option to use multiple tubes with space for inserts.
    [Corpus_Designer_v2.scad]
2022-06-30 Update Filter_Designer.scad
    Added Option to remove the hole structure and the option to change the bar type.
    [Filter_Designer.scad]
2022-06-30 Fixed insert slot
    [Corpus_Designer_v2.scad]
2022-06-30 Update Corpus_Designer_v2.scad
    Added Cube that can be used to darken up the plexi glass cube.
    [Corpus_Designer_v2.scad]
2022-06-30 replaced security bars with triangles for every but the last bars to improve printability.
    [Corpus_Designer_v2.scad]
2022-06-30 fixed Darkener design
    [Corpus_Designer_v2.scad]
2022-07-18 Updated Darkener
    [Corpus_Designer_v2.scad]
2022-07-18 added option to choose either the corpus, darkener or funnel
    [Corpus_Designer_v2.scad]
2022-08-05 Added funnel design to Corpus_Designer
    [Corpus_Designer_v2.scad]
2022-08-08 Added Concentric Filter Design
    [Filter_Designer.scad]
2022-08-08 changed slides model to accomodate bigger gap between slides
    [Filter_Designer.scad]
2022-08-09 Update Filter_Designer.scad
    Changed the slide to no longer get smaller to the middle
    [Filter_Designer.scad]
2022-08-09 Update Filter_Designer.scad
    Added offset from center for slides
    [Filter_Designer.scad]
2022-08-10 Update Filter_Designer.scad
    Added triangle filter structure
    [Filter_Designer.scad]
2023-06-26 Added option for brushes on Corpus
    [Corpus_Designer_v4.scad]
2023-11-19 Update Filter_Designer.scad
    Updated variables for easier use of the customizer, added groups and descriptions
    [Filter_Designer.scad]
2023-11-19 Update Corpus_Designer.scad
    Added variables for easier use of the Customizer
    [Corpus_Designer.scad]
2023-11-19 Removed redundant files
    [Corpus_Designer_v2.scad, Corpus_Designer_v4.scad]
2023-11-19 Added presets for the filter_designer
    [Filter_Designer.scad]
2023-11-20 Update README.md
    updated material recommendation
2023-11-22 added STL Files
    [Corpus.stl, Corpus_Brush.stl, Corpus_sans_holes.stl, Darkener.stl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]
2024-05-16 added version with acrylic cube on both ends
    [Corpus_Double_Cube.stl, corpus_designer.scad]
